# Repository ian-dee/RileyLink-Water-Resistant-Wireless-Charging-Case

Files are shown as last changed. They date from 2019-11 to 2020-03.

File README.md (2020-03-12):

# RileyLink-Water-Resistant-Wireless-Charging-Case
Water Resistant Wireless Charging Case for the RileyLink

This repository is for Drawing & STL files used to make the production version of the W2 case found on GetRileyLink.org. This case will fit both Medtronic or Omnipod versions of the RileyLink1.0 Board. The only difference between these files and the production version, is the omission of the Barometric Vent hole in the open source version. This is because the Barometric Vent is not an off the shelf component, and would be impossible for a maker to source. The case will still work as intended without the hole, but the case will need to be "burped" of pressure as the top is being put on. 

There are 5 Rev C Files: 

1. PDF Drawing showing the exploded view of the case (W2_RevC-OpenSource_No_Vent.PDF) 

2. 3 STL Files (Bottom_Shell_C.STL , Top_Shell_Common_C.STL , WC_Insert_C.STL)

3. Excel File BOM with purchase links to Wireless charging circuit, O-Rings, kapton tape, etc. (W2_Open_BOM.xls)

If you wish to purchase a complete kit to retrofit your RileyLink 1.0, with case made in injection molded polycarbonate, please visit https://getrileylink.org/product/w2case

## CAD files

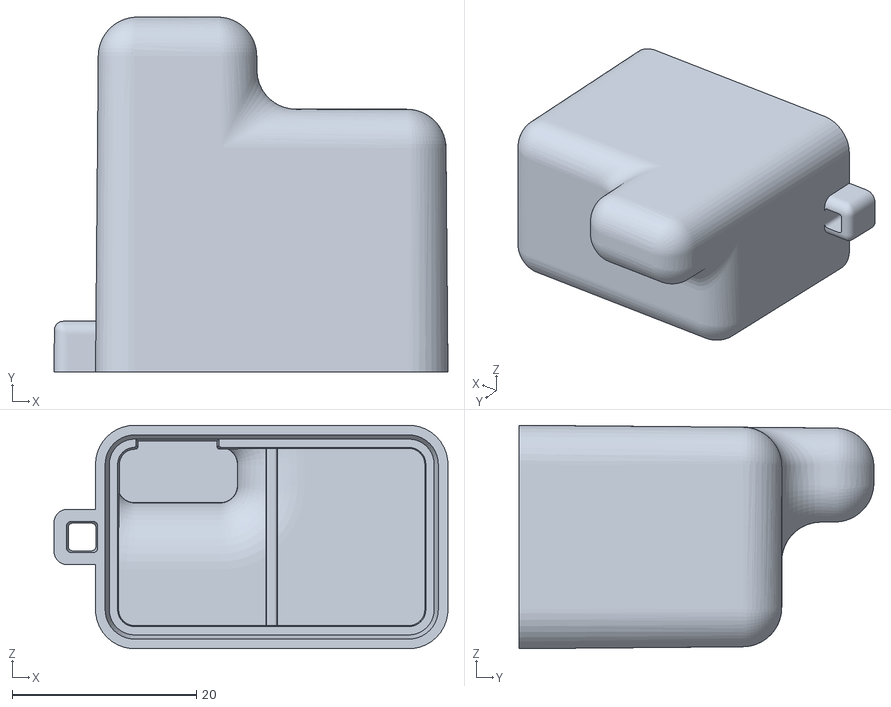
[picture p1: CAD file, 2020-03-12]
Top_Shell_Common_C.STL
42.8 x 38.5 x 24.3

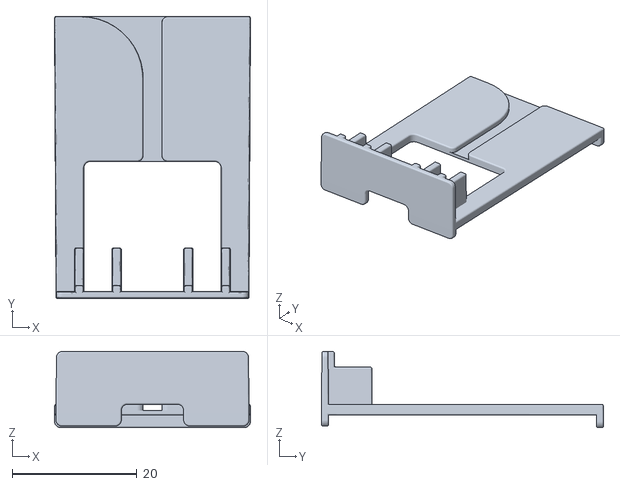
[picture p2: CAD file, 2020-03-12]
WC_Insert_C.STL
31.5 x 45.3 x 12.2

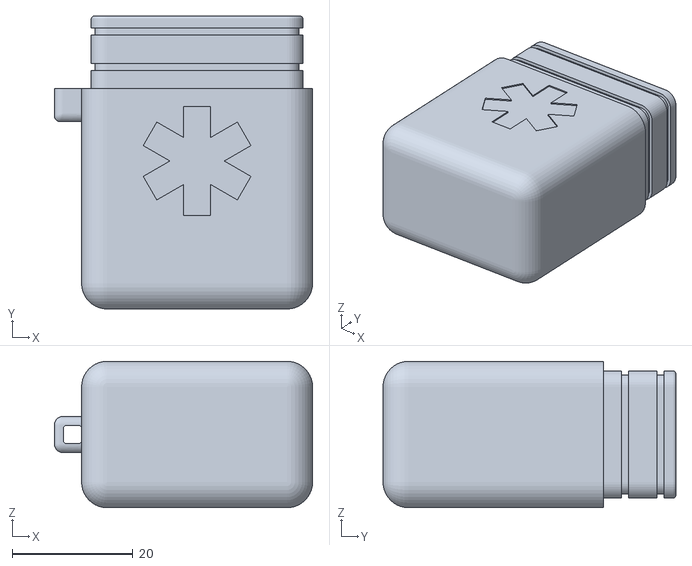
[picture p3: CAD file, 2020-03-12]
Bottom_Shell_C.STL
42.8 x 48.5 x 24.2

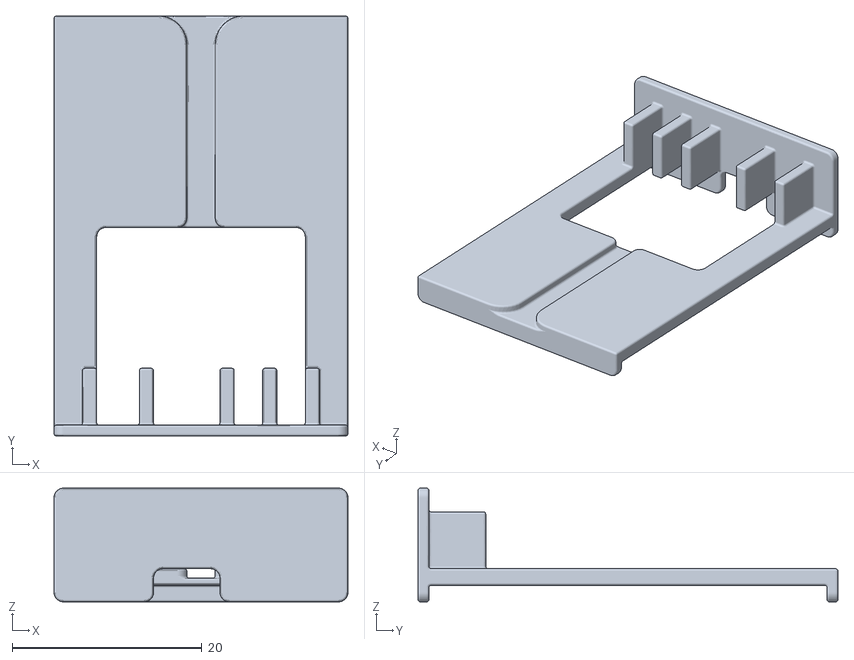
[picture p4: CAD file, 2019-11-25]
Op_Wireless_Insert_Sub_V2.STL
31.0 x 44.3 x 12.0

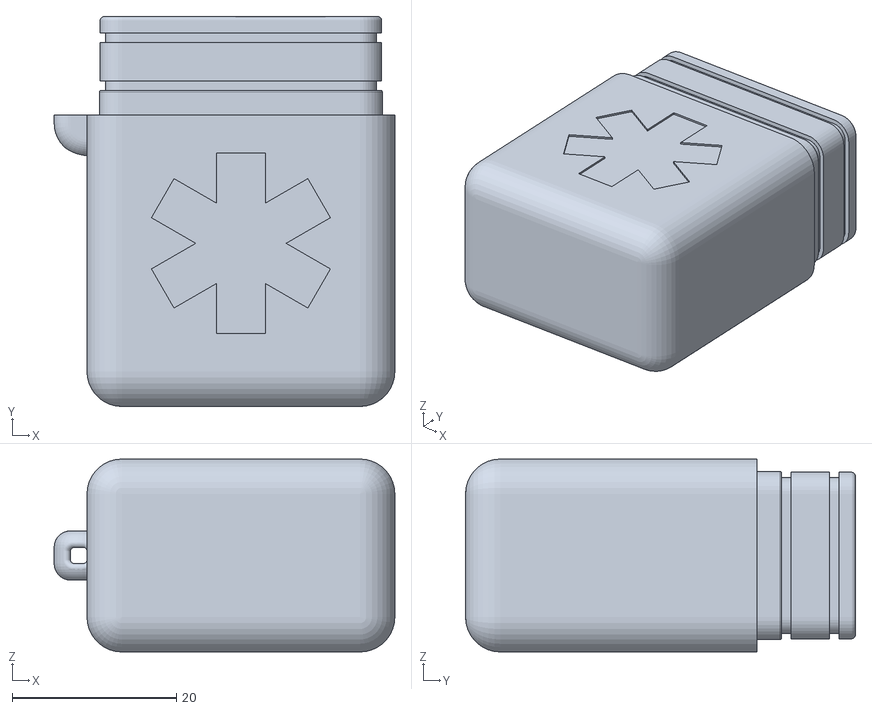
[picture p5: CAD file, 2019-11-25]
Op_Wireless_Shell_Bottom_V2.STL
41.5 x 47.5 x 23.5

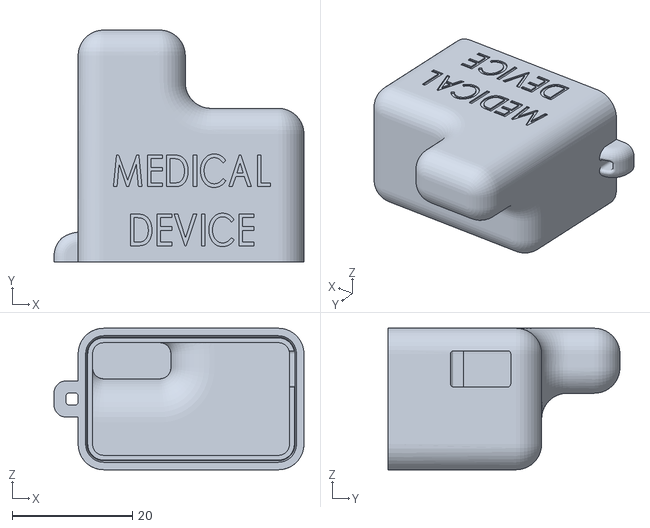
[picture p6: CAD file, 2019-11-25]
Op_Wireless_Shell_Top_USB_V2.STL
41.5 x 38.5 x 23.5

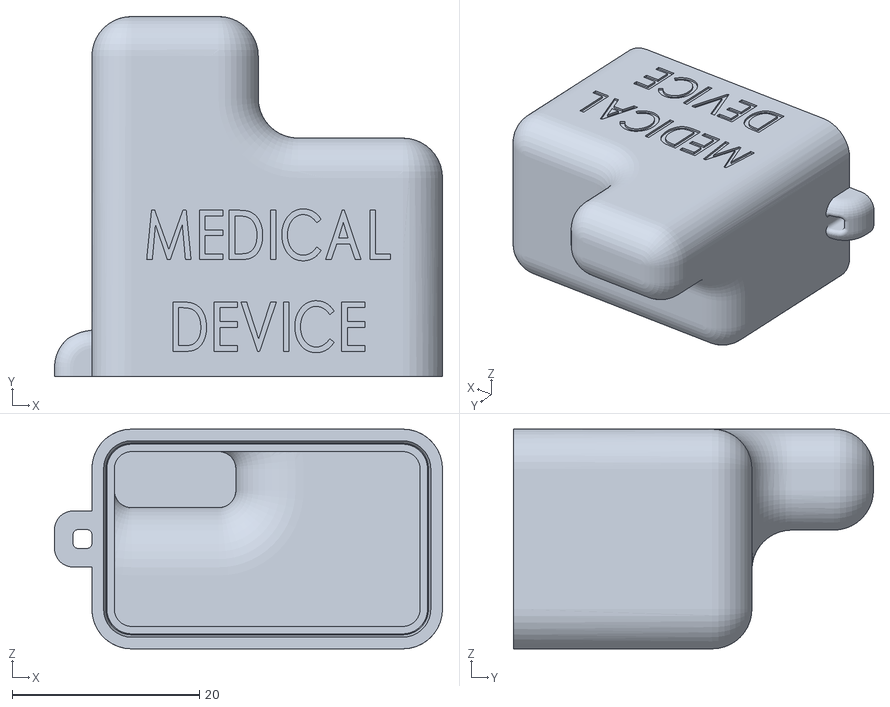
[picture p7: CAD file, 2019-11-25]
Op_Wireless_Shell_Top_V2.STL
41.5 x 38.5 x 23.5

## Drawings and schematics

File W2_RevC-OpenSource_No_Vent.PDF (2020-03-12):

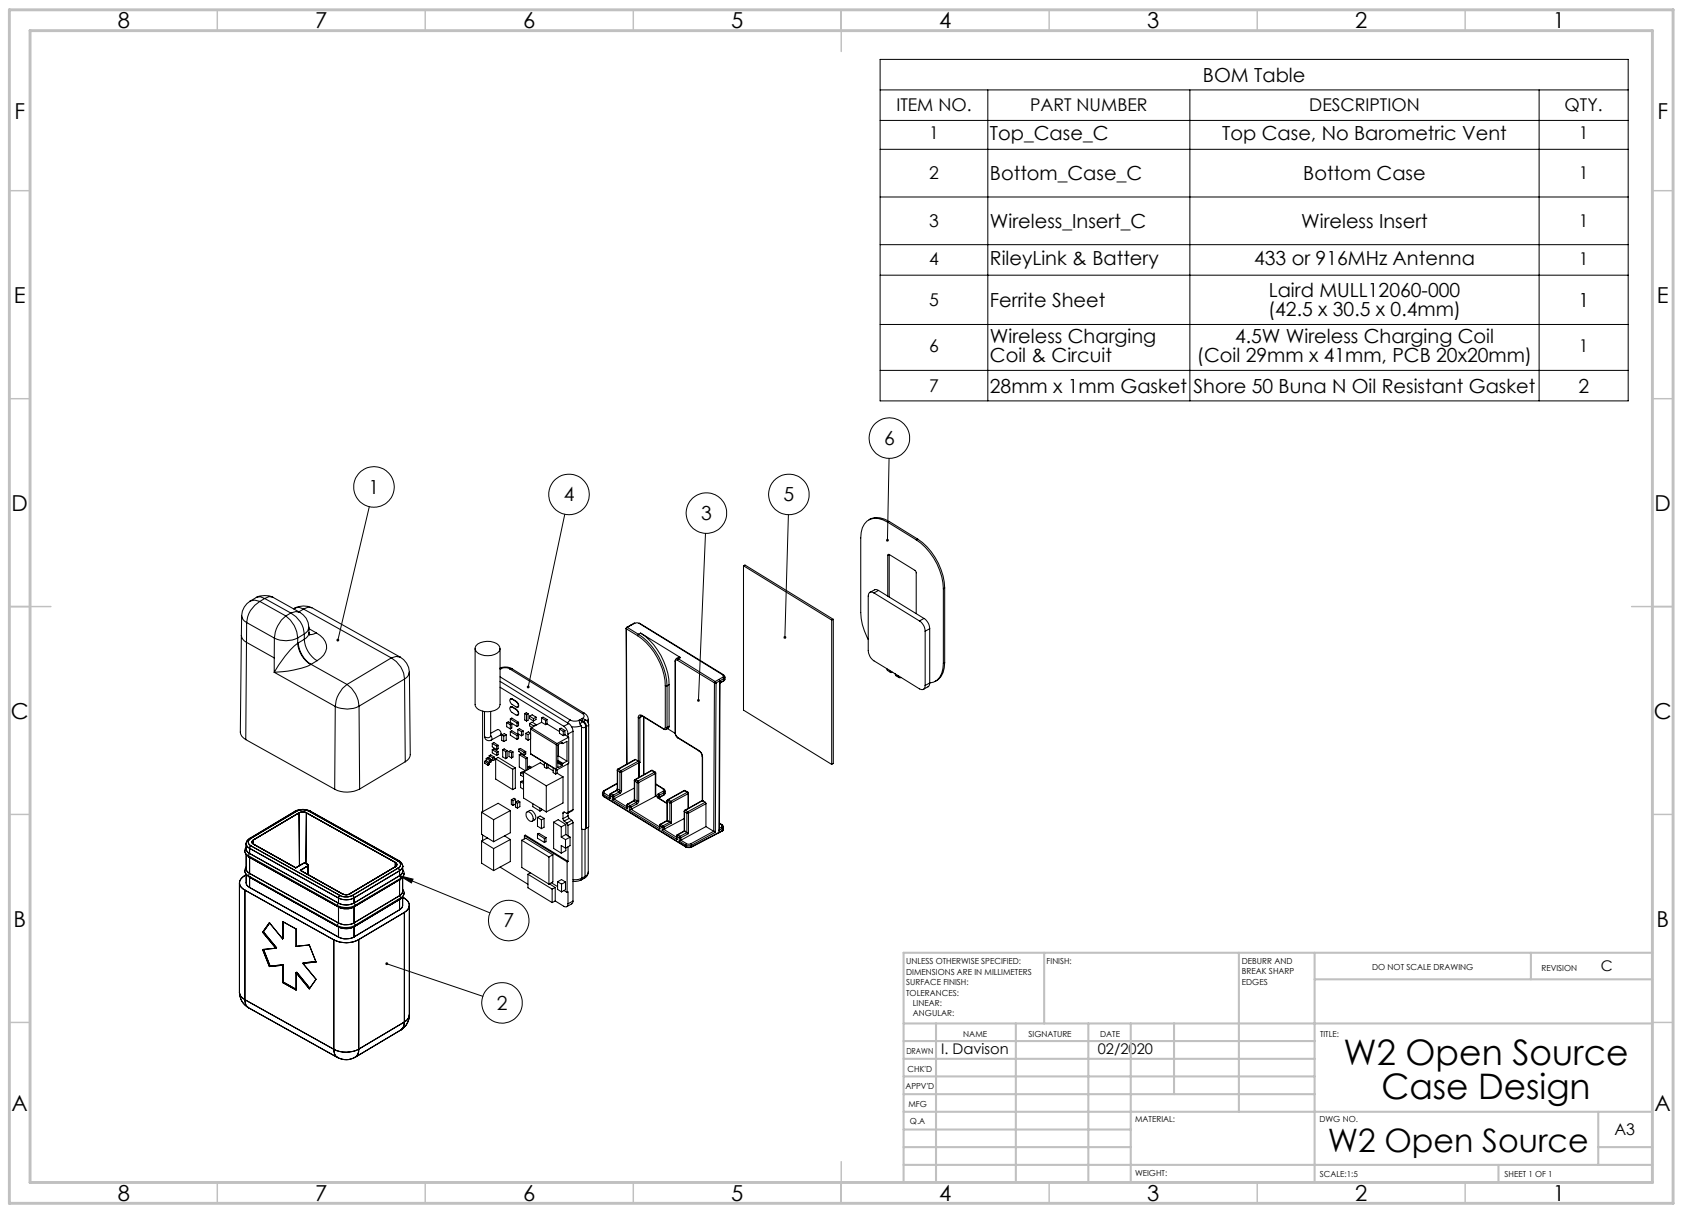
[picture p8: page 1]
BOM Table; FINISH:; DEBURR AND; BREAK SHARP; DO NOT SCALE DRAWING; REVISION; SCALE:1:5; SHEET 1 OF 1

ITEM NO. | PART NUMBER | DESCRIPTION | QTY.
1 | Top_Case_C | Top Case, No Barometric Vent | 1
2 | Bottom_Case_C | Bottom Case | 1
3 | Wireless_Insert_C | Wireless Insert | 1
4 | RileyLink & Battery | 433 or 916MHz Antenna | 1
5 | Ferrite Sheet | Laird MULL12060-000 (42.5 x 30.5 x 0.4mm) | 1
6 | Wireless Charging Coil & Circuit | 4.5W Wireless Charging Coil (Coil 29mm x 41mm, PCB 20x20mm) | 1
7 | 28mm x 1mm Gasket Shore 50 Buna N Oil Resistant Gasket | | 2

UNLESS OTHERWISE SPECIFIED:
DIMENSIONS ARE IN MILLIMETERS
SURFACE FINISH:
TOLERANCES:
LINEAR:
ANGULAR:

NAME | SIGNATURE | DATE | | | | TITLE: W2 Open Source Case Design
DRAWN | I. Davison | | 02/2020

CHK'D
APPV'D
MFG
Q.A | | | | MATERIAL: | DWG NO. W2 Open Source | A3

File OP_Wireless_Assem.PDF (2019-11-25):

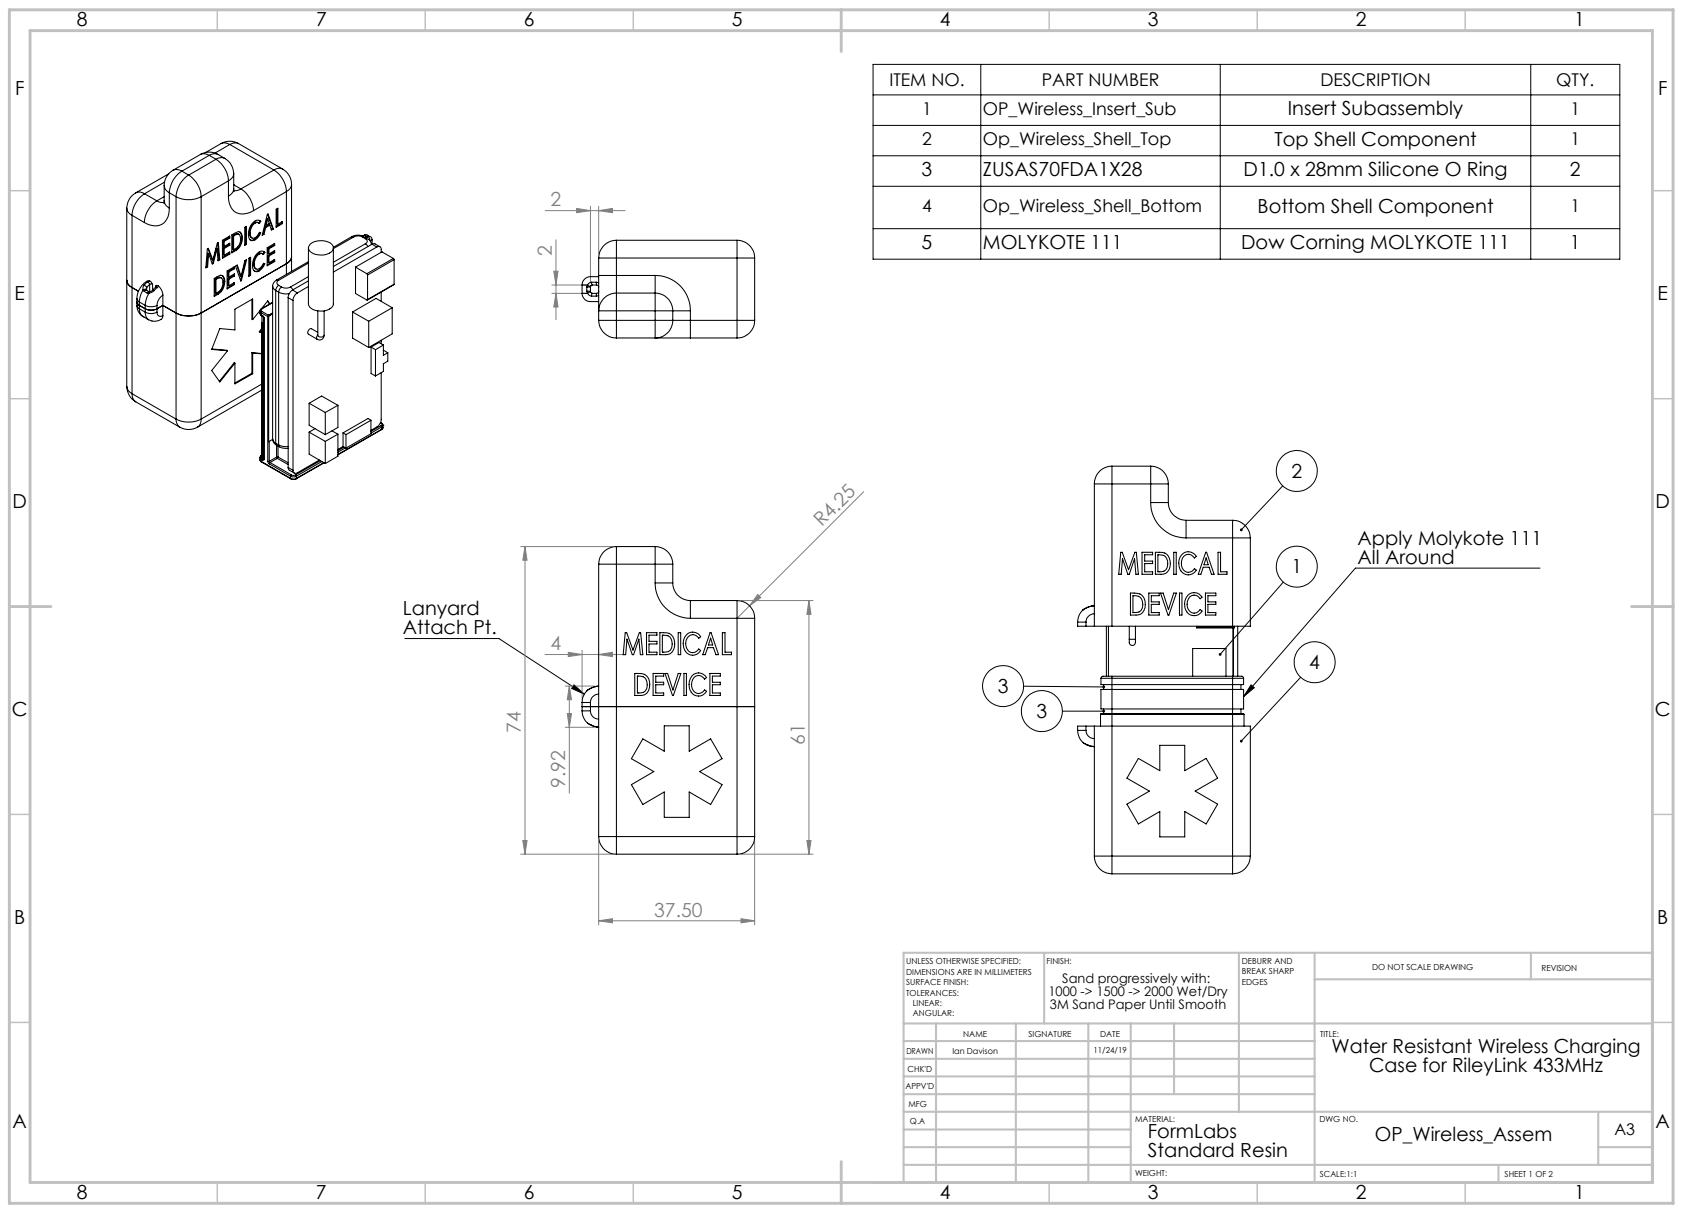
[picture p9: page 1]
Attach Pt.; Apply Molykote 111 All Around; FINISH:; DEBURR AND; BREAK SHARP; DO NOT SCALE DRAWING; REVISION; SCALE:1:1; SHEET 1 OF 2

ITEM NO. | PART NUMBER | DESCRIPTION | QTY.
1 | OP_Wireless_Insert_Sub | Insert Subassembly | 1
2 | Op_Wireless_Shell_Top | Top Shell Component | 1
3 | ZUSAS70FDA1X28 | D1.0 x 28mm Silicone O Ring | 2
4 | Op_Wireless_Shell_Bottom | Bottom Shell Component | 1
5 | MOLYKOTE 111 | Dow Corning MOLYKOTE 111 | 1

UNLESS OTHERWISE SPECIFIED:
DIMENSIONS ARE IN MILLIMETERS
SURFACE FINISH:
TOLERANCES:
LINEAR:
ANGULAR:

Sand progressively with:
1000 -> 1500 -> 2000 Wet/Dry
3M Sand Paper Until Smooth

NAME | SIGNATURE | DATE | | | | TITLE: Water Resistant Wireless Charging Case for RileyLink 433MHz

DRAWN | Ian Davison | | 11/24/19
CHK'D
APPV'D
MFG
Q.A | | | | MATERIAL: FormLabs Standard Resin | DWG NO. OP_Wireless_Assem | A3

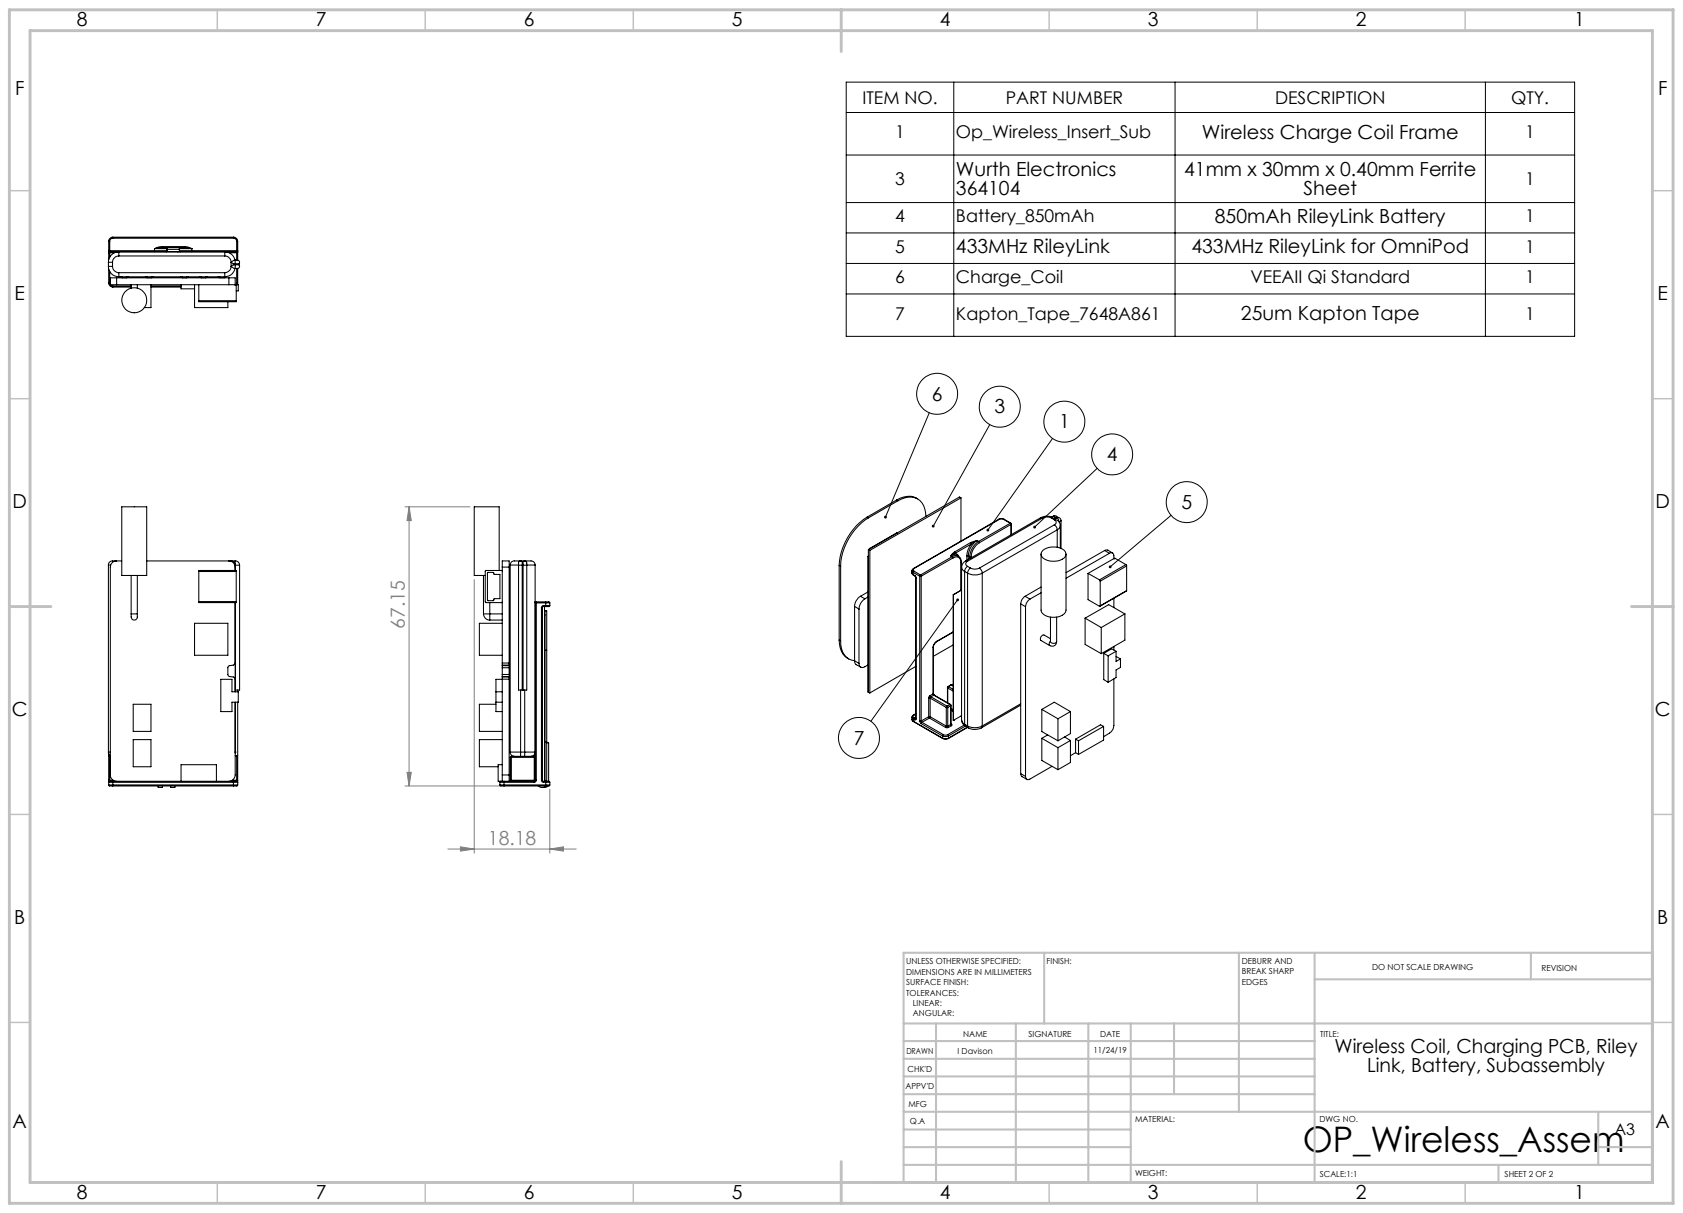
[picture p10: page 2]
FINISH:; DEBURR AND; BREAK SHARP; DO NOT SCALE DRAWING; REVISION; SCALE:1:1; SHEET 2 OF 2

ITEM NO. | PART NUMBER | DESCRIPTION | QTY.
1 | Op_Wireless_Insert_Sub | Wireless Charge Coil Frame | 1
3 | Wurth Electronics 364104 | 41mm x 30mm x 0.40mm Ferrite Sheet | 1
4 | Battery_850mAh | 850mAh RileyLink Battery | 1
5 | 433MHz RileyLink | 433MHz RileyLink for OmniPod | 1
6 | Charge_Coil | VEEAII Qi Standard | 1
7 | Kapton_Tape_7648A861 | 25um Kapton Tape | 1

UNLESS OTHERWISE SPECIFIED:
DIMENSIONS ARE IN MILLIMETERS
SURFACE FINISH:
TOLERANCES:
LINEAR:
ANGULAR:

NAME | SIGNATURE | DATE | | | | TITLE: Wireless Coil, Charging PCB, Riley Link, Battery, Subassembly

DRAWN | I Davison | | 11/24/19
CHK'D
APPV'D
MFG
Q.A | | | | MATERIAL: OP_Wireless_Assem | DWG NO. | A3

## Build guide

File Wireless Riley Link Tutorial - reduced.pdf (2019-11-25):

Wireless Charging RileyLink Case | I. Davison

## Purpose:

The purpose of this document is to act as a guide to replicate a prototype water resistant wireless charging case for a 433MHz RileyLink (OmniPod Version). This case has not been tested with a 916MHz (Medtronic) RileyLink.

## Means of Manufacture:

The original design was created using a FormLabs Form 2 (SLA 3D Printer). I highly
recommend using an SLA type printer with better than 100µm accuracy. This design is too precise for a run of the mill FDM, and the surface finish quality of FDM will not result in an acceptable gasket mating surface. Higher durability models may be made with other means of manufacturing such as resin casting or injection molding.

## Water Resistance:

If the design is made as intended, I would conservatively rate it to IPX4 (Protects from splashing water, no matter the direction). Do not go swimming with this case, set your basal rates correctly and leave it on shore!

## Wireless Charging:

The wireless charging functionality is designed for use with Qi Wireless chargers. However, it is not extremely tolerant to placement inaccuracy - i.e. you must find the “sweet spot” location on the wireless charging pad that results in the RileyLink charge indicator shining the brightest. If you place it too far outside of the “sweet spot”, the device will stop charging after 30s or so. The receiver coil in the case must be aligned directly above the coil in your charging pad ±5mm for optimal results. You will notice the LED on the RileyLink shine brightest when you’ve found the “sweet spot”.

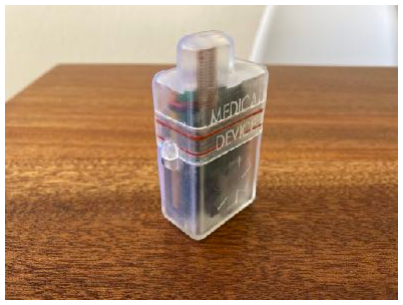
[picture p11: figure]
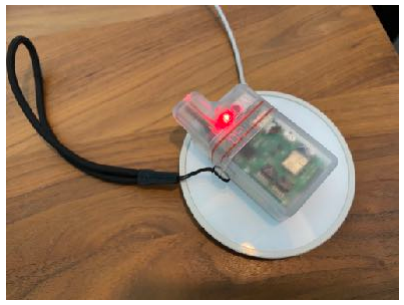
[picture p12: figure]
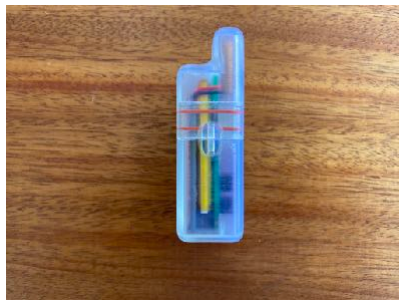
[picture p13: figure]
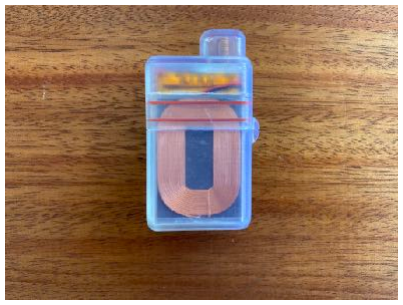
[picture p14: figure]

Revision 1 | 11/25/2019 | Page 1 of 10

## Bill of Materials:

Besides the cost of the 3D printed hard shells, the device can be constructed with approximately $200 of materials, including the cost of the RileyLink. (which includes a battery and Lanyard) Links to all materials are included in the BOM table below.

Bill of Materials

Part | No Per Unit | Manufacturer | Part No | Description | Vendor | Link | MOQ | No of Units per MOQ | Cost Per MOQ
Rileylink | 1 | RileyLink | | 433MHz OmniPod | RileyLink | https://getrileylink.org/product/rileylink433 (https://getrileylink.org/product/rileylink433) | 1 | 1 | $150.00
Top Shell | 1 | DS-LLC | | Wireless Charging Case Top Shell | TBD, SLA | https://github.com/ian-dee/RileyLink-Water-Resistant-Wireless-Charging-Case/tree/ (https://github.com/ian-dee/RileyLink-Water-Resistant-Wireless-Charging-Case/tree/master) master | N/A | 1 | N/A
Bottom Shell | 1 | DS-LLC | | Wireless Charging Case Bottom Shell | TBD, SLA
Insert | 1 | DS-LLC | | Wireless Charging Case Insert Frame | TBD, SLA
O Ring | 2 | USA Sealing | ZUSAS70 FDA1X28 | 28mm x Ø1.0mm Silicone Gasket | McMaster Carr | https://www.mcmaster.com/5233t123 (https://www.mcmaster.com/5233t123) | 25 | 12 | $8.45
Ferrite | 1 | Wurth | 364104 | RF Ferrite Sheet 60mm x 60mm x 0.5mm with PSA backer | DigiKey | https://www.digikey.com/products/en?mpart=364104&v=732 (https://www.digikey.com/products/en?mpart=364104&v=732) | 1 | 2 | $8.74
Wireless Coil | 1 | VEEAII | N/A | VEEAII Qi Standard Wireless Charging DIY Coil Receiver Module | Ali Express (Qi Charger Store) | https://www.aliexpress.com/item/33002939788.html (https://www.aliexpress.com/item/33002939788.html) | 1 | 1 | $3.68
Kapton Tape | 1 | Dupont | | Kapton® Polyimide Plastic 63µm Thickness | McMaster Carr | https://www.mcmaster.com/7648a735 (https://www.mcmaster.com/7648a735) | 15ft | 60 | $12.75
Molykote 111 | 1 | Dow Corning | 111 | Dow Molykote 111 Silicone Lubricant | Amazon | https://www.amazon.com/1310476-Molykote-Valve-Lubricant-Sealant/dp/B00IKUIO82/ (https://www.amazon.com/1310476-Molykote-Valve-Lubricant-Sealant/dp/B00IKUIO82/) | 1 | 200 | $15.74
| Subtotal Cost, not including 3D Printed Parts | | | | | | | | $199.36

### 1.0 Assembly Tutorial

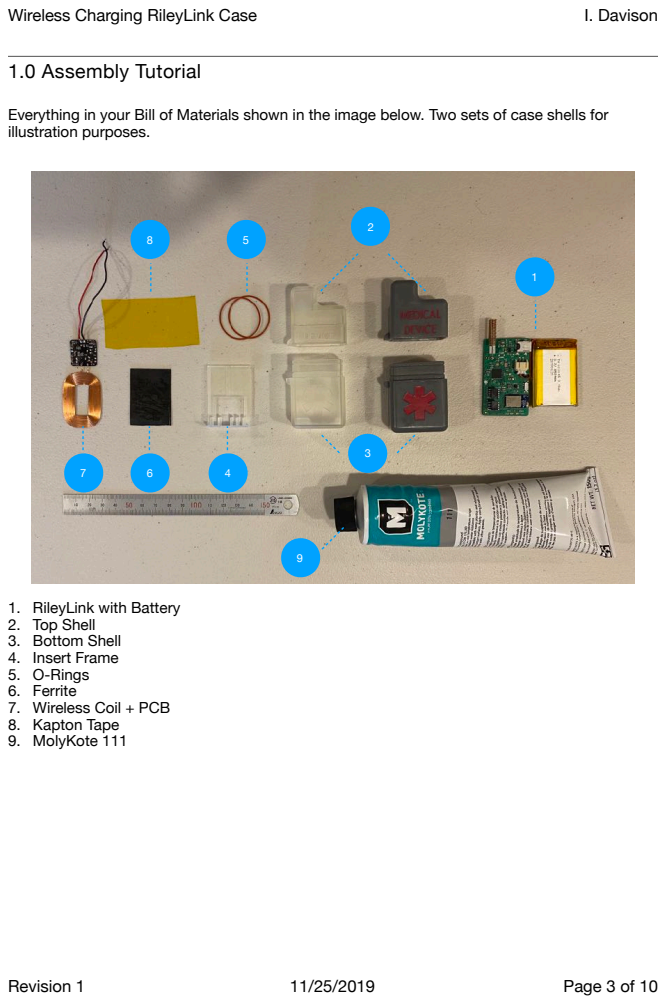
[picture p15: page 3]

Everything in your Bill of Materials shown in the image below. Two sets of case shells for
illustration purposes.

1. RileyLink with Battery
2. Top Shell
3. Bottom Shell
4. Insert Frame
5. O-Rings
6. Ferrite
7. Wireless Coil + PCB
8. Kapton Tape
9. MolyKote 111

### 2.0 Build the Wireless Charging Subassembly Insert

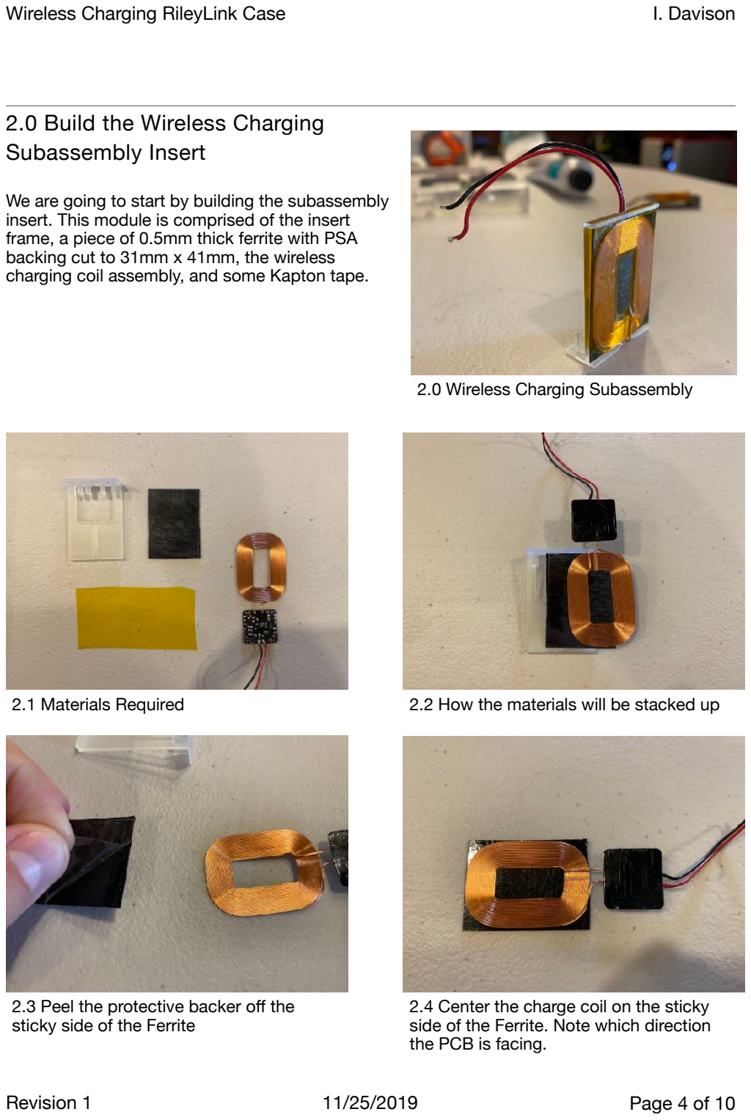
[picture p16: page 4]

We are going to start by building the subassembly insert. This module is comprised of the insert frame, a piece of 0.5mm thick ferrite with PSA backing cut to 31mm x 41mm, the wireless charging coil assembly, and some Kapton tape.

2.0 Wireless Charging Subassembly

2.1 Materials Required | 2.2 How the materials will be stacked up

2.3 Peel the protective backer off the sticky side of the Ferrite

2.4 Center the charge coil on the sticky side of the Ferrite. Note which direction the PCB is facing.

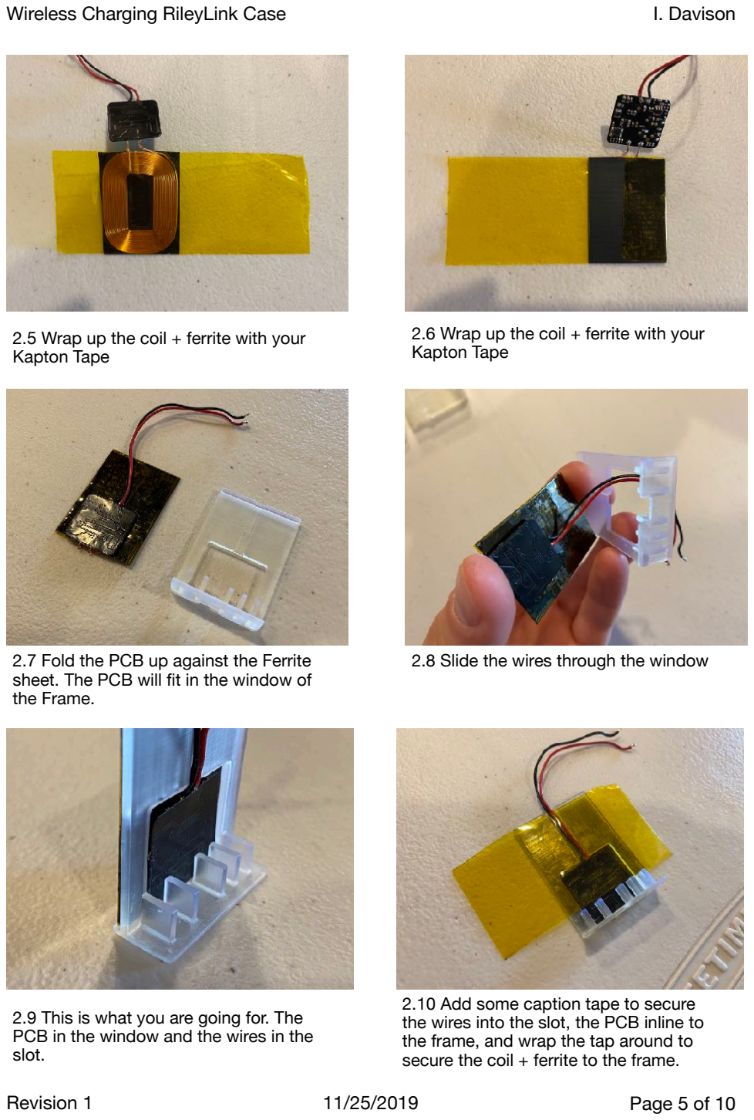
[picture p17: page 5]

2.5 Wrap up the coil + ferrite with your Kapton Tape

2.6 Wrap up the coil + ferrite with your Kapton Tape

2.7 Fold the PCB up against the Ferrite sheet. The PCB will fit in the window of the Frame.

2.9 This is what you are going for. The PCB in the window and the wires in the slot.

2.8 Slide the wires through the window

2.10 Add some caption tape to secure the wires into the slot, the PCB inline to the frame, and wrap the tap around to secure the coil + ferrite to the frame.

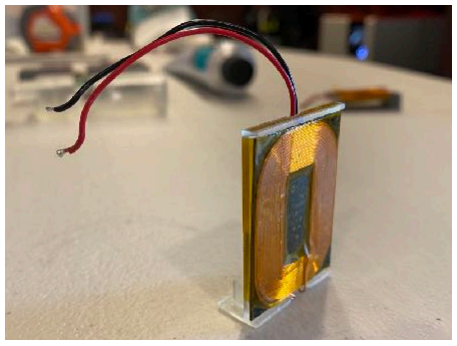
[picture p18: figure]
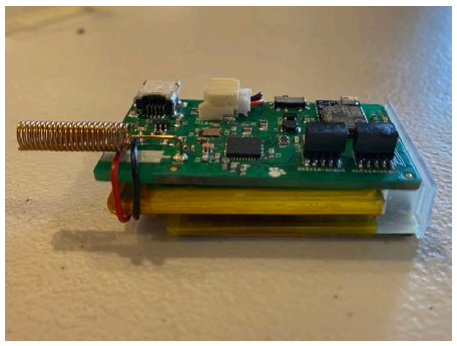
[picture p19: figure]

### 3.0 Assembling the Charging Coil to your RileyLink

Next step is to make a sandwich out of the wireless charging subassembly you just built, the Battery, and the RileyLink Board. Soldering will be required for this step.

2.11 A nice little wireless charging coil subassembly package. Now would be a good time to test it with the MultiMeter on your charging pad before moving to the next step.

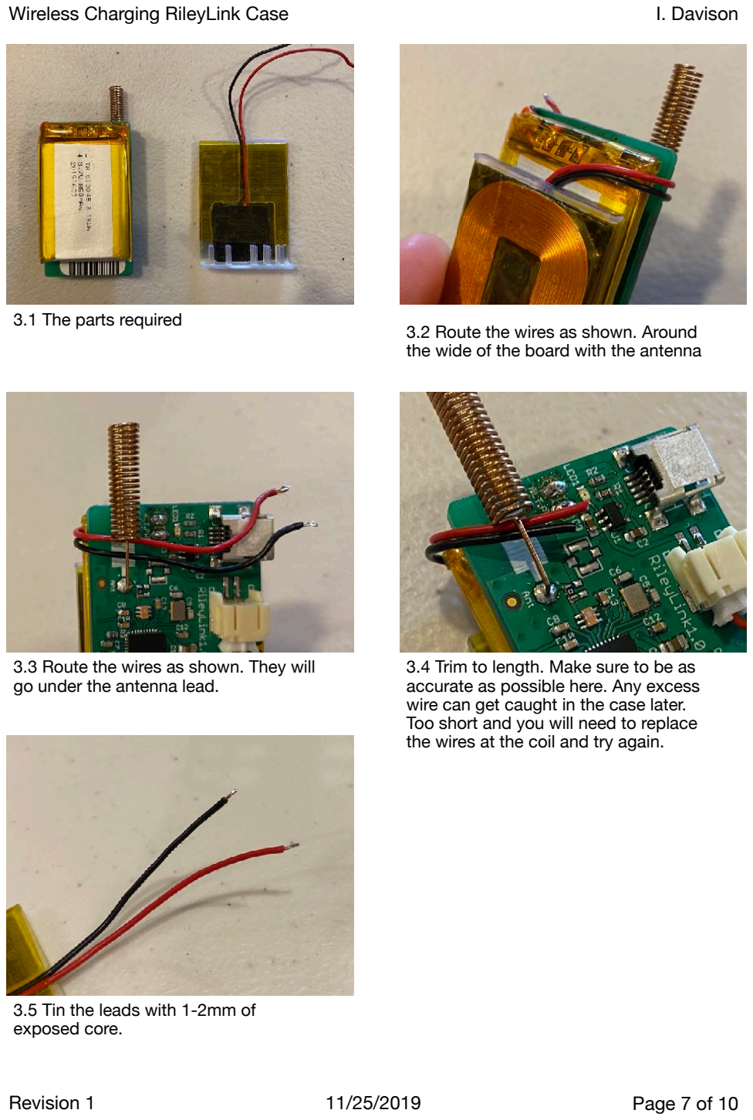
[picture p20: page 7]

3.1 The parts required | 3.2 Route the wires as shown. Around the wide of the board with the antenna

3.3 Route the wires as shown. They will go under the antenna lead.

3.4 Trim to length. Make sure to be as accurate as possible here. Any excess wire can get caught in the case later. Too short and you will need to replace the wires at the coil and try again.

3.5 Tin the leads with 1-2mm of exposed core.

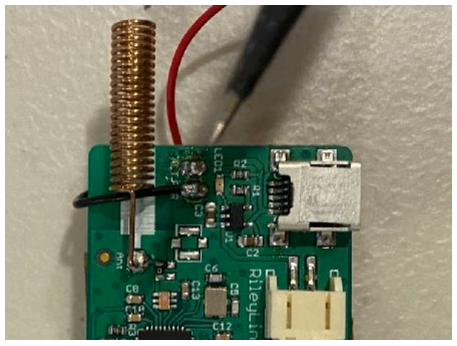
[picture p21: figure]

3.6 Make sure the board is off and battery is disconnected. Solder the Black ( - ) Lead to the lower auxiliary power input pad on the RileyLink Board, and the Red (+) Lead to the upper. It is easier to solder black then red due to board layout and proximity to other components.

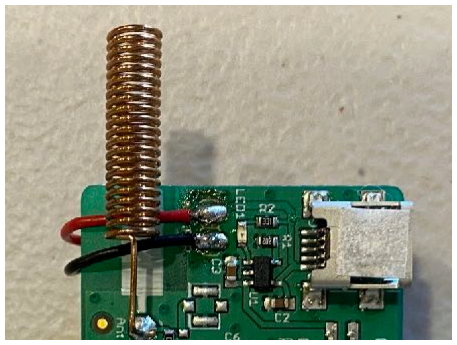
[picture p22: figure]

3.7 All Done

### 4.0 Assembling the Enclosure

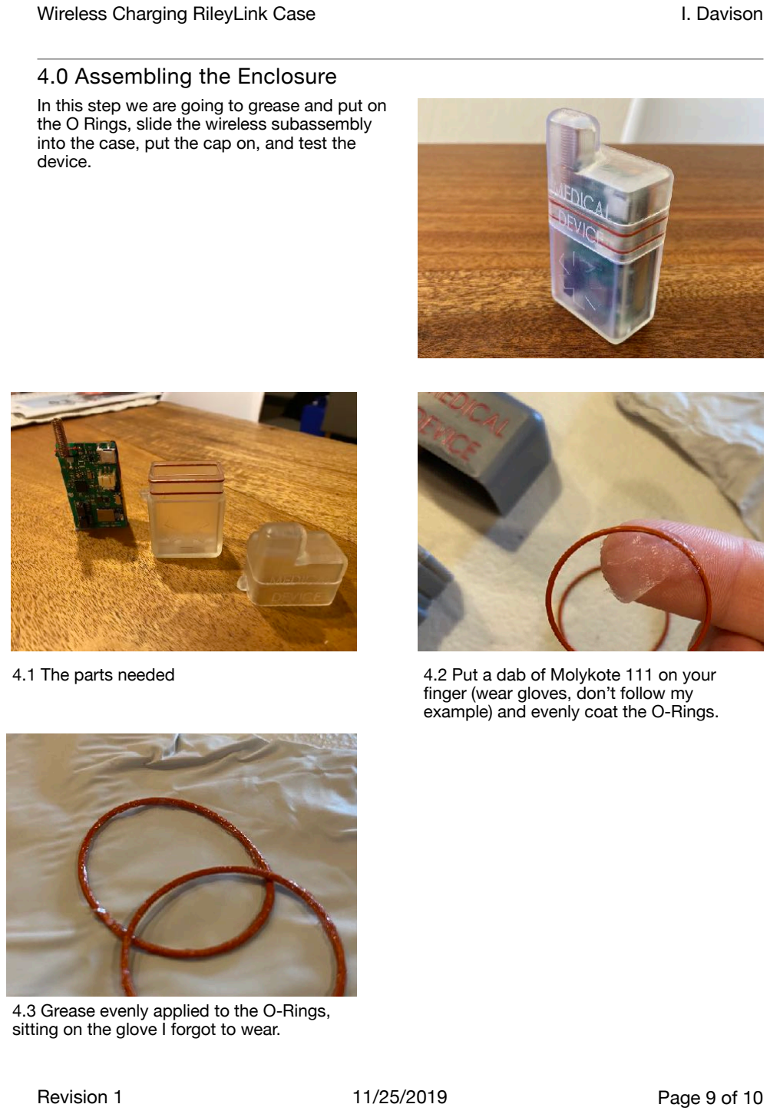
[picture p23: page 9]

In this step we are going to grease and put on the O Rings, slide the wireless subassembly into the case, put the cap on, and test the device.

4.1 The parts needed | 4.2 Put a dab of Molykote 111 on your finger (wear gloves, don’t follow my example) and evenly coat the O-Rings.

4.3 Grease evenly applied to the O-Rings, sitting on the glove I forgot to wear.

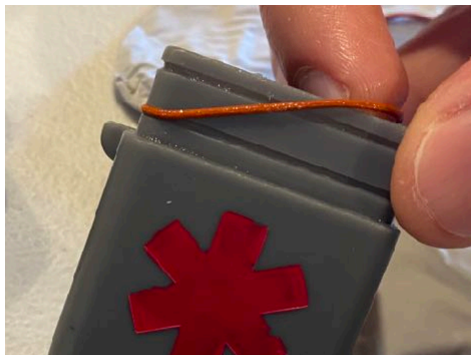
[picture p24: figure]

4.4 Place the O-Rings into the glands on the bottom case by stretching over the top. Be sure not to twist the O-Rings.

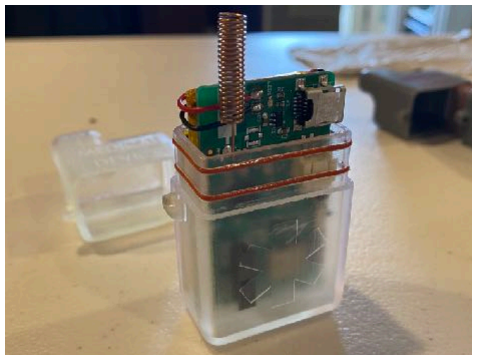
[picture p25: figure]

4.5 Carefully slide the Wireless Subassembly into the case, with the RileyLink PCB facing towards the “Star of Life”, and the charging coil side facing away. The wireless subassembly won’t fully seat, and your top won’t close if you try to put it in the case backwards.

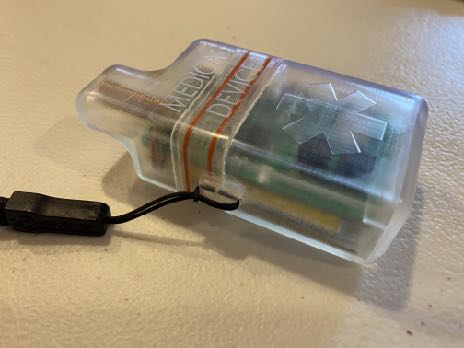
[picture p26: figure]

4.6 Put the top on and install the Lanyard if desired. Note: The seal between upper and lower halves may be so good that the case builds pressure when assembling the top. It may try to push the top off. Try rocking the cap left and right to “burp” the pressure out (let the internal air go past the seals) while putting the top on. The pressure will equalize over time. I am not sure how this case will work on an airplane, the pressure delta may work to force the top off if no Lanyard is used.

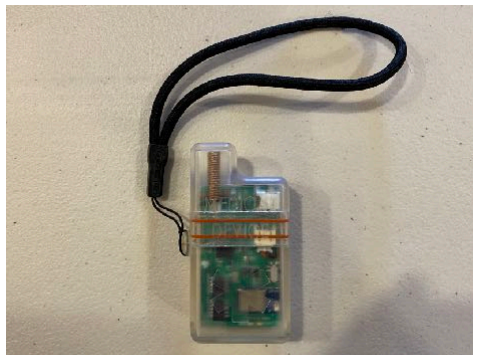
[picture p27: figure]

4.7 All finished! Note: I would not advocate hanging this device on the outside of a bag or otherwise with the lanyard. I would only use it to secure it to the inside of your bag (like to a key clip in a backpack) or locate the device more easily. It is certainly possible in the right situation the lanyard clip could break off, resulting in loss of your device.

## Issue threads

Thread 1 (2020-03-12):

### ISSUE TITLE
Barometric vent

### ISSUE THREAD

**Issue by ToreBj** [ian-dee/RileyLink-Water-Resistant-Wireless-Charging-Case#1]
I can't see the barometric vent in the BOM. Neither is there any opening for one in the STL file?

**Comment by ian-dee** [comment]
HI Tore, correct. There is no B-Vent in the open source version of the case, since the vent itself is not an off the shelf component and would be impossible for others to order at a low minimum order quantity. The case will work without a B Vent, but will hold air pressure that needs to be burped out as the cap is put on. For the mass production variant I opted to add a B-Vent so the cap can easily be put on without burping air, and to keep the pressure equalized to the environment when traveling on airplanes, changing elevation, etc.

**Comment by ToreBj** [comment]
👍 Thanks for what looks like a new and very useful option. I'm doing what I can for my local community providing them with 3D printed stuff for free. The tough case has been very popular lately. Take care in these Corona times 😁

**Comment by ian-dee** [comment]
Thats great! Please note - I am planning to upload the common case design that supports both medtronic & Omnipod versions of the RileyLink. The version that is up now is great for Omnipod, but is a very tight fit for the Medtronic. I'll upload today - will be Rev C

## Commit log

2019-11-25 Add files via upload
    PreForm (Print Software for Form Labs Printers) with optimized support structure locations. This is V1 - the only changes from V1 - V2 are minor tweaks to internal radii that reduce material use and 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
2019-11-25 Add files via upload
    Wireless Charging Case Assembly Tutorial
2020-03-12 Rev C: Production Version of W2 Case but no B-Vent
    Rev C is the production version of the W2 case available on getrileylink.org, but without the Barometric Vent hole in the top case. The case will fit both Medtronic and Omnipod RileyLink 1.0 boards, 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
    [Bottom_Shell_C.STL, Top_Shell_Common_C.STL, WC_Insert_C.STL]
2020-10-30 W2 Clip Final Tooled Design
    This is the final design of the W2 Clip, a belt clip for the W2 Case. The part was tooled up in injection molded polycarbonate and is available for purchase on www.getrileylink.org. For those attempt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
